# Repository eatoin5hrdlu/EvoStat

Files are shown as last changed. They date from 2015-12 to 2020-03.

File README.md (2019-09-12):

EvoStat:  A PhageStat to support PACE and PATHE Experiments
====
Software and Hardware for an automated platform for PACE and PATHE experiments.

PATHE (Phage-Assisted Three-Hybrid Evolution) is our enhancement to PACE (Phage Assisted Continuous Evolution) which was described by Kevin M. Esvelt, Jacob C. Carlson, and David R. Liu in http://www.ncbi.nlm.nih.gov/pubmed/21478873

This project contains Arduino code for a Host CellStat (Turbidostat), Sample Collector, and Lagoons
as well as the server software to provide an on-screen interface to Temperature, Turbidity, Flowrate,
and Sample Collector control and Web interface.  The goal is a remote access, fully automated system with a build cost less than $1000.00. 

SWI-Prolog based web server, GUI, and Turbidostat control software written mostly in Prolog/Xpce with some Python (e.g. pySerial, for a 
portable serial interface to Arduino) and HTML. Bluetooth interface added as foreign function library to SWI-Prolog currently eliminates the need for pySerial. See github.com/eatoin5hrdlu/plblue 

Running EvoStat on a Linux or Windows machine provides an interface for multiple phageStats with Bluetooth connected Arduinos running module.ino (then software defined as Host or Lagoon controller) and a sample collector: Bluetooth connected Arduino running collector.ino. (Using a WiFi camera and bluetooth modules has reduced apparatus wiring by 90%)

A web interface provides a similar interface via the URL:  

    http://<host>:21847/web/pathe.pl

Prerequisite Software
====
- Python2.7
- OpenCV (on Linux add "apt-get install python-opencv")
- SWI-Prolog with Xpce
- Arduino IDE (Processing)
- apt-get install these additional packages
  - python-psutil, ffmpeg, octave, dnsutil  (some other stuff, watch this space).
  - On Linux add : imagemagick (for conversion of image files)
  - apache2-utils: for Web Authentication (encrypted password) Files
  - 

Getting Started
====
1) Clone the EvoStat repo:

    git clone https://github.com/eatoin5hrdlu/EvoStat.git

2) Create a "secrets" file in the EvoStat directory to enable sending of SMS messages

Filename :       secrets
File contents:   { 'login': 'your-email', 'password': 'your-password' }

   Example: For gmail, your-email does not include "@gmail.com"
   Your login is just the first part of your email address
    
3) Clone the plblue Git repository (Prolog interface to Bluetooth communication)

    git clone https://github.com/eatoin5hrdlu/plblue.git
    
    cd plblue
    
    make      ( required packages: libbluetooth-dev and bluez )
    
    make install  (moves the shared library into the ../EvoStat directory

--- MESSAGING (SMS) via Python smstext.py program
Needs package dnsutil for program "dig" to get outside IP address, in order to include a functional URL for the EvoStat to outside users.

File 'secrets' must have login/password for SMS server (e.g. via gmail)

--- LEVEL detection Python/OpenCV

A python program (alevel.py) uses OpenCV to read the liquid levels of the vessels.
Windows and linux versions of #! in ipcam.py appear at the top of the file
It may be necessary to move the correct one to the top. Or call python:

$ python level.py 
$ python level.py show -c 30 sample.jpg
OPTIONS: -c N repeat in N seconds (default 90)
         show   (produce debugging output, including processed images)
         <filename>.jpg    (Read the image file instead of the camera /dev/video{0,1,2} )

------------------
Create stand-alone executable "evostat" (Prolog saved-state)
$ swipl (linux) or swipl-win
:- [c].
:- save_evostat.

Or to maintain terminal access for debugging, start with:

$ swipl(-win)
:- [c].
:- c.

When the interface comes up, you can:
turn off the automatic level sensing with Action -> Stop
turn off the PID volume/flow controllers  Action -> PIDstop
Get back to the Prolog prompt with File -> OK

View the Web Interface with the URL  http://localhost:21847/web/pathe.pl

The unusual port numbers are from the ca. 1995 NetSpeak (WebPhone). My legacy, no longer in use.
Change it in c.pl to 80 or 8080 to appear as a normal web server

--------------
To changing the Icon on a Prolog saved-state on Windows:

    chicon.exe saved.exe myapp.ico myapp.exe

###########################
Procedure for operating the EvoStat:

Sterilize Supply and Drain Valves with 1M NaOH

Install Valves

Autoclave Cellstat and Lagoon vessels

Autoclave Nutrient/Inducers in conainers

Install supply vessels on top of EvoStat and connect to supply valves

Connect supply valves to Cellstat

Open bypass valve to fill Cellstat with Nutrient

Close bypass valve when Cellstat Level is at desired set point (85%)

Inject host cells into Cellstat when target temperature is reached.

Normal flow control begins when OD target has been reached.

Infect lagoons with phage.

Regular texts will be sent to report EvoStat status.
	Each text includes the URL to EvoStat status/control page.
Exceptional texts will be sent if:
	1) temperature / turbidity / level / flow out of range
	2) leak has been detected

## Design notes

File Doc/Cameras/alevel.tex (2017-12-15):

\documentclass[10pt,letterpaper]{article}
\usepackage[top=0.85in,left=2.75in,footskip=0.75in]{geometry}
\usepackage{amsmath,amssymb}
\usepackage{changepage}
\usepackage[utf8]{inputenc}
\usepackage{textcomp,marvosym}
\usepackage{cite}
\usepackage{nameref}
\usepackage[pdftex,
            pdfauthor={Peter Reintjes},
            pdftitle={EvoStat Level Monitoring System},
            pdfsubject={Level Monitoring},
            pdfkeywords={OpenCV Python},
            pdfproducer={Latex with hyperref},
            pdfcreator={pdflatex}]{hyperref}

\hypersetup{
    colorlinks=true,
    linkcolor=blue,
    filecolor=magenta,      
    urlcolor=cyan,
}
\usepackage[right]{lineno}
\usepackage{microtype}
\DisableLigatures[f]{encoding = *, family = * }
\usepackage[table]{xcolor}
\usepackage{array}
\usepackage{listings}
\newcolumntype{+}{!{\vrule width 2pt}}
\newlength\savedwidth
\newcommand\thickcline[1]{%
  \noalign{\global\savedwidth\arrayrulewidth\global\arrayrulewidth 2pt}%
  \cline{#1}%
  \noalign{\vskip\arrayrulewidth}%
  \noalign{\global\arrayrulewidth\savedwidth}%
}

% \thickhline command for thick horizontal lines that span the table
\newcommand\thickhline{\noalign{\global\savedwidth\arrayrulewidth\global\arrayrulewidth 2pt}%
\hline
\noalign{\global\arrayrulewidth\savedwidth}}

\usepackage{enumitem}
\setlist{nosep}
\raggedright
\setlength{\parindent}{0.5cm}
\textwidth 5.25in 
\textheight 8.75in

\usepackage[aboveskip=1pt,labelfont=bf,labelsep=period,justification=raggedright,singlelinecheck=off]{caption}
\renewcommand{\figurename}{Fig}

% Remove brackets from numbering in List of References
\makeatletter
\renewcommand{\@biblabel}[1]{\quad#1.}
\makeatother

% Leave date blank
\date{}
% Header and Footer with logo
\usepackage{lastpage,fancyhdr,graphicx,wrapfig}
\usepackage{epstopdf}
\pagestyle{myheadings}
\pagestyle{fancy}
\fancyhf{}
\setlength{\headheight}{27.023pt}
%\lhead{\includegraphics[width=2.0in]{PLOS-submission.eps}}
%\rfoot{\thepage/\pageref{lastpage}}
\renewcommand{\footrule}{\hrule height 2pt \vspace{2mm}}
\fancyheadoffset[L]{2.25in}
\fancyfootoffset[L]{2.25in}
% customize
\lfoot{\sf Innatrix Internal Document}

\begin{document}

\title{EvoStat Level Monitoring System}
\author{Peter Reintjes}
\date{\today}
\maketitle

\vspace*{0.2in}
\begin{flushleft}
.jpg}
\end{flushleft}

{\it The EvoStat liquid-level control system consists of two distict parts: Monitoring and Control, which are accomplished by separate programs.  This report focuses on the monitoring program (alevel.py), a Python/OpenCV\cite{opencv} program which observes and reports the levels of vessels within the main EvoStat chamber.  The main EvoStat control program requires this level information to maintain volumes, cell density, and flow rates in the various chambers to support experiments in the continuous evolution of bacteriophage\cite{pace}.}

\section*{Introduction}

The {\bf alevel.py} program is a Python program which takes an image from a digital camera and determines the individual liquid levels in transparent containers within the image.  The EvoStat system uses the program to report the liquid levels of up to five vessels, one 2-liter host-cell cultivator and four 250mL lagoons.

\section*{Level Detection in the EvoStat}
Whenever a level reading is to be taken, {\bf alevel.py} reads a text file {\bf .previous} which specifies for each vessel:

\begin{enumerate}[itemsep=1pt, topsep=2pt, partopsep=0pt]
\item Area of the image in which the meniscus appears
\item Recommended intensity amplification (images to sum)
\item Recommended contrast (gain and threshold) settings
\end{enumerate}
Here is an example of the {\bf .previous} file containing the recommended settings and vessel locations.  The {\bf reticule} entry refers to the red reference LEDs used for level calibration.  The absence of a bounding box indicates that the reticules can be anywhere within the image area.
\begin{verbatim}
# (Vessel,oldPt,BBox,Contrast-iter, Contrast-mul, Contrast-off,')
#               Erode-iter, Dilate-iter, Amplify-iter, Amp-factor')
# (name, (x,y), ((uy,lx),(ly,rx)), 1, 1.2, -80, 2, 2, 3, 0.7)')
# lagoon   1, 1.5972, -90, 2, 2, 3, 0.7)]
[('reticule', 0, 1.4, -80, 180, 1, 4, 3, 0.4),
 ('host0', (47, 22), ((40, 120), (214, 380)), 1, 1.2, -80, 2, 2, 2, 0.4),
 ('lagoon1', (84, 71), ((340, 50), (460, 260)), 1, 1.1, -110, 2, 2, 3, 0.7)]
\end{verbatim}

The file is named {\bf .previous} because the program will try these recommended values for contrast and intensity settings but vary them until it can get a good level reading.  If the user specified the {\bf update} option when invoking {\bf alevel.py} a new file will be written with the contrast and intensity values actually used.  The next time the program is run, these settings may be able to get a good level reading without the need to vary them.  The program may also adjust the bounding boxes to be smaller and centered on the meniscus that was actually measured.

\subsection*{Camera Settings}
The unusual (low) light conditions inside the EvoStat may require a camera to be initialized with specific exposure, contrast, and saturation settings. While many cameras have automatic exposure modes, detection can often be improved with custom settings to match the dark conditions and our use of primary colors: red for the reticules, green for the liquid menisci.

One of the legacies of
Windows\textsuperscript{\textregistered}
and other closed systems is that each camera manufacturer has to produce a program for the (closed) operating system for each of their cameras.  Linux systems have kept up pretty well with a tool called guvcview which knows about many cameras -- especially the cheap ones.  This interactive program can be used to modify settings on many cameras and save those settings in a file with the {\bf .gpfl} suffix.  This file can be used to initialize the camera when the program starts by calling the program {\bf uvcdynctrl}.

After making the necessary image adjustments to the camera at {\bf /dev/video0} with {\bf guvcview} and saving the settings in the file {\bf evostat.gpfl}, the level monitor program (or any other process) can run the following command to restore the camera to these settings:
\begin{verbatim}
       /usr/bin/uvcdynctrl -L evostat.gpfl --device=/dev/video0
\end{verbatim}

Although the EvoStat programs are otherwise portable between Linux and
Windows\textsuperscript{\textregistered}
systems, we know of no comparable program that would make this method
of camera initialization available on
Windows\textsuperscript{\textregistered}
systems.

\subsection*{Alignment}
It is not necessary to align the camera precisely as long as it has a clear view of the reticule column and that the regions specified for each vessel in the {\bf .previous} file surround a sufficient horizontal region of the meniscus.

\subsubsection*{The Reticules}
The {\bf reticules} are movable red LED assemblies on a black column inside the EvoStat. The upper assembly should be aligned with the target liquid level in the upper, or host-cell cultivation chamber, while the lower assembly should be aligned with the target level for the lagoons.  The EvoStat is designed so that all of the lagoons are on the same level, hence we only need one reticule to provide a reference for the lagoon levels.

\begin{wrapfigure}{L}{0.25\textwidth}
\centering
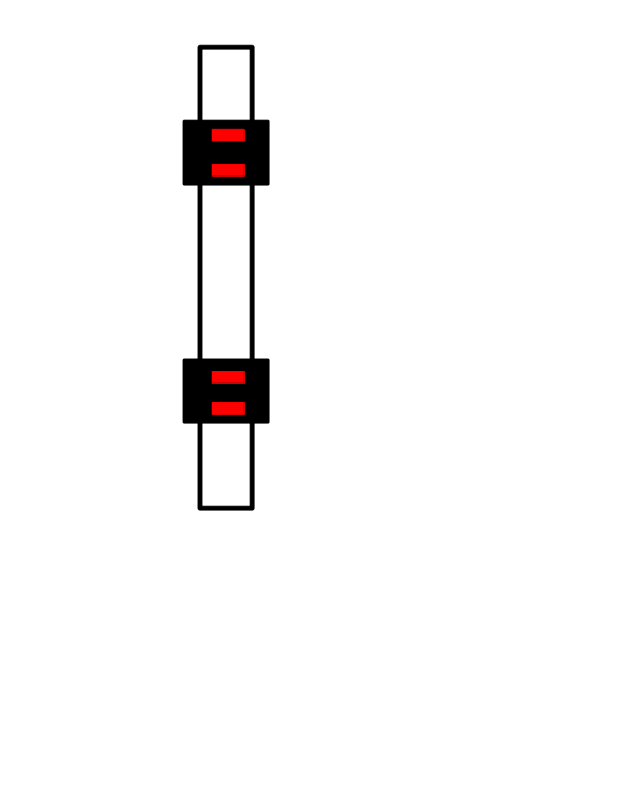
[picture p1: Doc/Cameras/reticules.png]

\caption{\label{fig:reticules}Reticules}
\end{wrapfigure}

Reticule placement does not directly specify the level being controlled.  Level control is relative to the reticules and may be set to maintain a level at an offset above or below the level of the reticule. In the simplist case, however, it is convenient to position the reticule assembly so that the two red bars surround (above and below) the desired liquid level.  This corresponds to a zero offset for the liquid level to be maintained.

\subsubsection*{Vessels}

For each vessel, the
{\bf .previous}
file has a bounding box defining the region of the image where the meniscus will be visible, and intensity and contrast settings. Once
{\bf alevel.py}
reads this file, it will try to detect the horizontal liquid level in each of these regions using the contrast and intensity settings found in the file. However, if this fails it will vary each of these parameters by positive and negative factors in 10\% increments until it gets a good reading (or a specified number of attempts have been made).  With the {\bf update} option,
{\bf alevel.py}
will re-write the new values to the
{\bf .previous}
file.

\subsection*{Lighting}

The various EvoStat vessel holders shine light from bright green LEDs up into the liquid containers. When liquids are clear (e.g. uninoculated), this results in a reflection off the meniscus which can be used to determine the liquid level. However, the system works most reliably with the turbidity of a growing culture which is the primary mode of EvoStat operation.  Until the image processing has been improved, we should consider that accurate level readings will only occur when there is active culture in the vessels (e.g. not during setup and sterility testing).

Level readings also fail when the EvoStat chamber is opened, and therefore exposed to normal room lighting.  While the ability to darken the room can substitute for a closed chamber, we haven't had that luxury since being evicted from the Tod Vision's gardening tool shed in the Genome Sciences Building.

If a good level reading is not possible, calls to the level monitoring program return no results and the EvoStat reacts as if the last good reading was repeated.  As with all other parts of the EvoStat, the system is designed to operate with the current settings through any loss of telemetry.

\subsection*{Growth Conditions}
Under actual growth conditions, the liquids are turbid and create a lot of scattered light.  The LEDs below the vessel must be bright enough to completely illuminate the contents.  This is particularly important for the large, upper chamber because the light source is at the bottom of the 2-liter container. In particular, we do not see a high-contrast meniscus when the volume is near the overflow drain (1.5 liter level).

\section*{Next Steps}

Now that the level reporting program is relatively stable, a complete code-review re-write is in order.  Duplicated code can be eliminated in the horizontal line detection and image amplification subroutines. Red/reticule and Green/Level readings had minor differences which were best debugged using separate implementations.

Produce level information in resolution independent coordinates so that they are the same whether a 640x480 or 1280x1024 image is available. Or, alternately, provide image resolution information with the data and allow the recieving program to do the coordinate mapping.

\begin{enumerate}[itemsep=1pt, topsep=2pt, partopsep=0pt]
\item Review/re-write code: 800 lines of Python, can probably be halved.
\item Make level data resolution independent
\item Automate camera settings under Windows\textsuperscript{\textregistered}
\end{enumerate}

\bibliographystyle{unsrt}
\bibliography{alevel}{}

\pagebreak

\section{Appendix: alevel.py source code}
\newcommand*{\SrcPath}{../..}
\lstinputlisting[language=Python]{\SrcPath/alevel.py}
\end{document}

\input{\MyPath/chap1/ch1.tex}

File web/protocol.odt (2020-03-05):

EvoStat (PACE) Protocol

Huxley Run #2 January 7-11 2019

January 2019

Su Mo Tu We Th Fr Sa

1 2 3 4 5

6 [7 8 9 10 11 12 ...]

13 14 15 16 17 18 19

20 21 22 23 24 25 26

27 28 29 30 31

[Notes]

7 L of LB (2X autoclave. Final cycle 45-min)

Kanamycin (water) : 30ug/mL →30mg/L → 210mg/7 L

JW5856 requires Kanamycin for the TRXA- “deletion” which is an insertion of kanamycin resistance gene.

( 30ug/mL is from Baba et al. 2006 )

Tetracycline : 10ug/mL → 10mg/L → 70mg/7 L

( for F+ maintenance )

Chloramphenicol (either, but ethanol better): 25ug/mL → 25mg/L → 175mg/7 L

Carbenicillin (water) : 60ug/mL → 60mg/L → 420mg/7 L

Glucose 175mL 20% by weight = .45% in 7 L (27mM)

HG-Selection Run in EvoStat: repeat of the previous run but with better flow control.

Cells: JW5856:t3trxA:MP6

Phage: M13T7rnaP

Ref: Jiarui’s lab report of Nov 13.

1. Grow JW5856+MP6 to 0.5 OD in chamber 1.
2. Transfer 40 ml from chamber 1 to lagoon
3. Add sufficient arabinose to bring the lagoon to 0.3% arabinose
4. ?? alternative here is to use ATc at 30 ng/ml
5. Add M13RNAP to the lagoon at an MOI of about 1.0 (previously used 0.5)
6. Start the run with flow through the lagoon at 30 ml per hour

Autoclave nutrient (LB) twice over the weekend, added Kanamycin, Tetracyline, Carbenicillin, Chlorophenicol, and 25mM Glucose (175mL of 20% by weight for 7L).

Inoculate with cells Sunday Evening

Infect with Phage Monday.

[ Previous run had one day sterility test, room temperature, without antibiotics ]

JW5856-2 M13 T7 RNA pol evolution run (Jan 6 to Jan 13 or extend…)

1. Pre-mutagenize M13T7RNAP:

Martha has grown M13 RNAP on S1030: MP6 in 2XYT added with tetracycline, chloramphenicol and 25mM arabinose for 5 hours, and clarified in 30 min/3.5k. The titer is 1.5E+10 pfu/ml.

2. Grow JW5856 T3-trxA+MP6 to 0.5 OD in chamber 1.
3. Transfer 40 ml from chamber 1 to lagoon.
4. Add sufficient arabinose to bring the lagoon to 0.3% arabinose.
5. Add M13RNAP to the lagoon at an MOI of about 1.0.
6. Make the virus and JW5856 cells incubate for 1. 5 hours in the lagoon.
7. Start the run with flow through the lagoon at 30 ml per hour.
8. Make the run continuously for at least 7 days. Every day, take samples to check Hibit expression, plaque on S1030, JW5856-2, and JW5856-2 MP6+T3 trxA.
9. When we see big increase for Hibit expression, or many plaques on S1030 and/or JW5856 MP6+T3 trxA, extract DNA from M13 RNAP, and do sequencing.

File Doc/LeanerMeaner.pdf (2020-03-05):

## Instructions for manual PACE/PATHE setup using peristaltic pumps and large incubation chamber

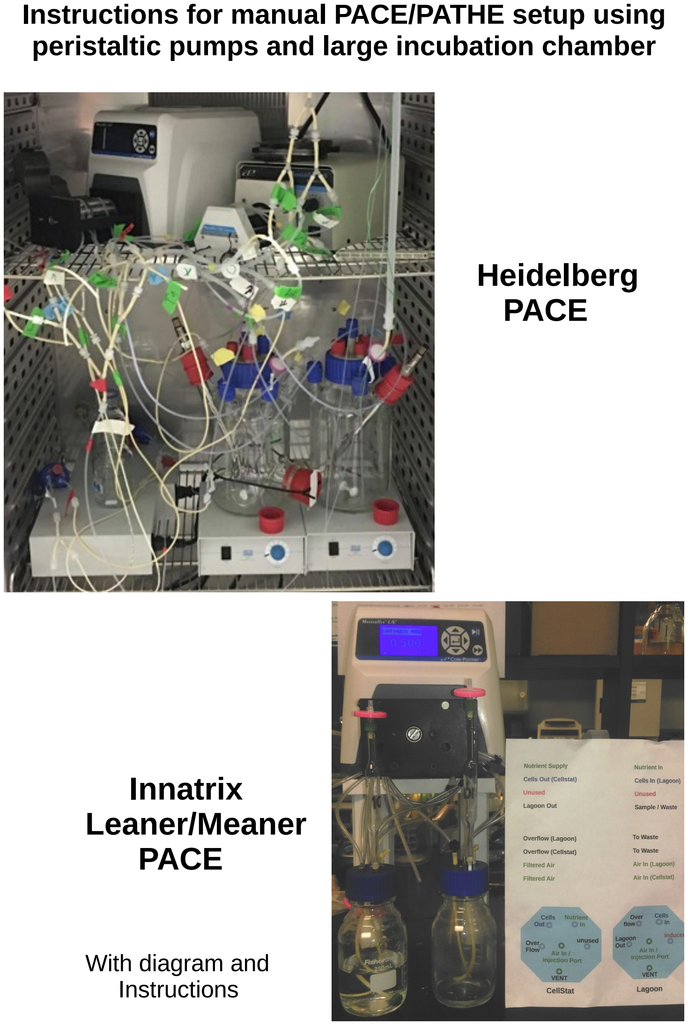
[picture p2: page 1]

## Heidelberg PACE

## Innatrix Leaner/Meaner PACE

### With diagram and Instructions

This setup uses seven (7) of the eight peristaltic pump channels. There may be hours between steps as they involve autoclaving, flling, and sterility testing. Filling steps can be accelerated by changing the pump speed.

Starting at the pump face and moving outward toward the observer, the pump channels are numbered 1-8. With the default mode of the pump moving liquid from left to right, we designate the ends of the tubes as [a] left/input and [b] right/output.

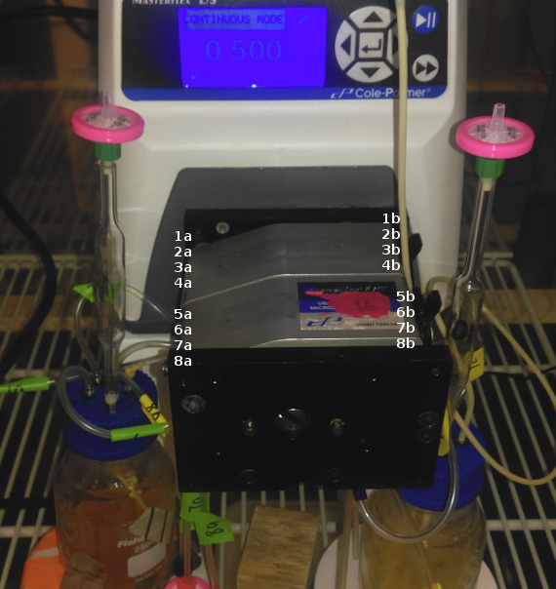
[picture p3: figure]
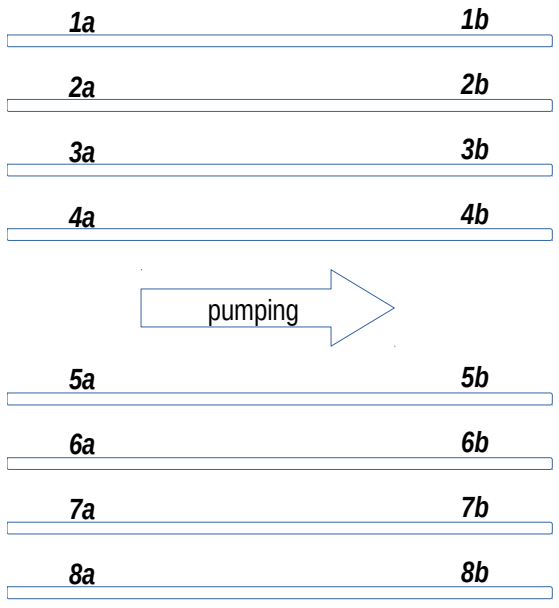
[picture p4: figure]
pumping

In the continuous evolution experiment, we make the following assignments.

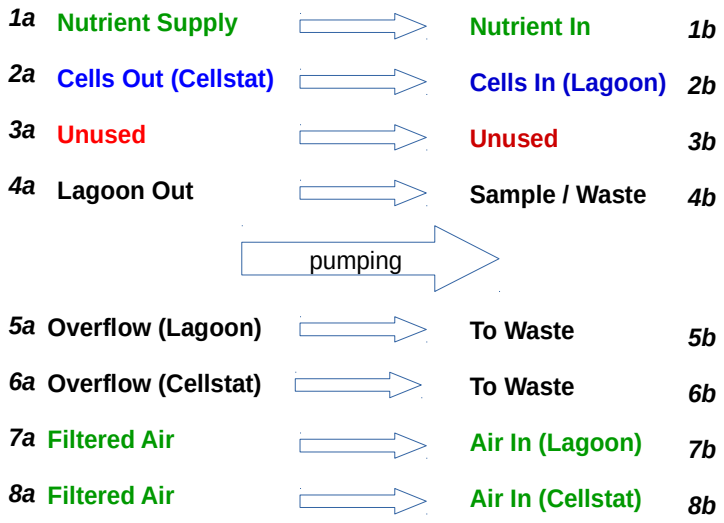
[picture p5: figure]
Nutrient Supply; Cells Out (Cellstat); Unused; Lagoon Out; Nutrient In; Cells In (Lagoon); Sample / Waste; Overflow (Lagoon); Overflow (Cellstat); Filtered Air; To Waste; Air In (Lagoon); Air In (Cellstat); pumping

Step 1: Sterilizing the Equipment

Autoclave vessels and place the [a] left/input ends of all pump tubes into an ethanol supply. Place [b] right/output ends of tubes into an ethanol receiver. Start pump.

Step 2: Initial Connections and Air Vents

With vessels still in the Autoclave, attach new 0.45 micron flters to the vent burets. Also install and verify direction of vents in Nutrient and Inducer vessels. Preferred air-fow direction in the 0.45 micron flters is into the luer connector and out through the nipple. Air intake is vital for Nutrient and Inducer supplies, while Air exhaust is required for CellStat and Lagoon. Each vessel must have either an intake or an exhaust flter.

Move vessels to incubator and place CellStat and Lagoon on stirring plates under pump.

Leave tubes 2a, 2b, and 4a in ethanol while removing other tubes from ethanol and connecting according to the labels in the diagram. Don’t forget to insert new 0.45 micron flters into tubes 7aa and 8a (SSterile Air Intake).

Allow CellStat to fill with Nutrient. Then, with heating, aeration, and mixing operational, remain in this state to verify CellStat sterility by turning the pump of (Note: this also turns aeration off, but if nothing is growing, the rate it isn’t growing doesnt matter).

Step 3: Innoculate CellStat

Add host cells to CellStat and wait for growth to OD600 of 0.4. Remove the buret air vent temporarily to inject cells. Pump is still of.

Step 4: Fill Lagoon

With CellStat at target volume, connect tubes 2a (SCells Out / CellStat) and 2b (SCells In / Lagoon) to begin flling Lagoon. Pump must be turned on.

Step 5: Infect and Start Continuous Flow

With Lagoon at target volume, infect Lagoon with phage via buret/air flter vent port and connect 4a (Lagoon Out) while making sure that 4b is connected to the waste/sample collector. Connect Inducer from the secondary pump (Snot shown) which will be supplying additional chemicals to the Lagoon.

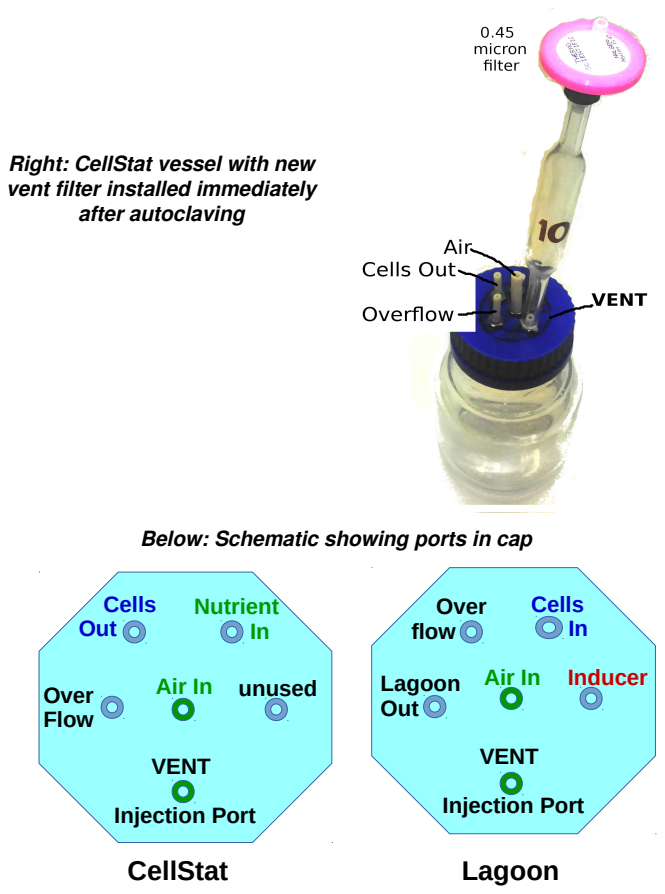
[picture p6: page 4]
after autoclaving; Lagoon Out; Over flow; Cells In; Inducer; VENT; Injection Port; Air In; Cells Out; Nutrient In; Over Flow; unused; CellStat; Lagoon

Right: CellStat vessel with new
vent filter installed immediately

Below: Schematic showing ports in cap

### Nutrient Supply

### Cells Out (Cellstat)

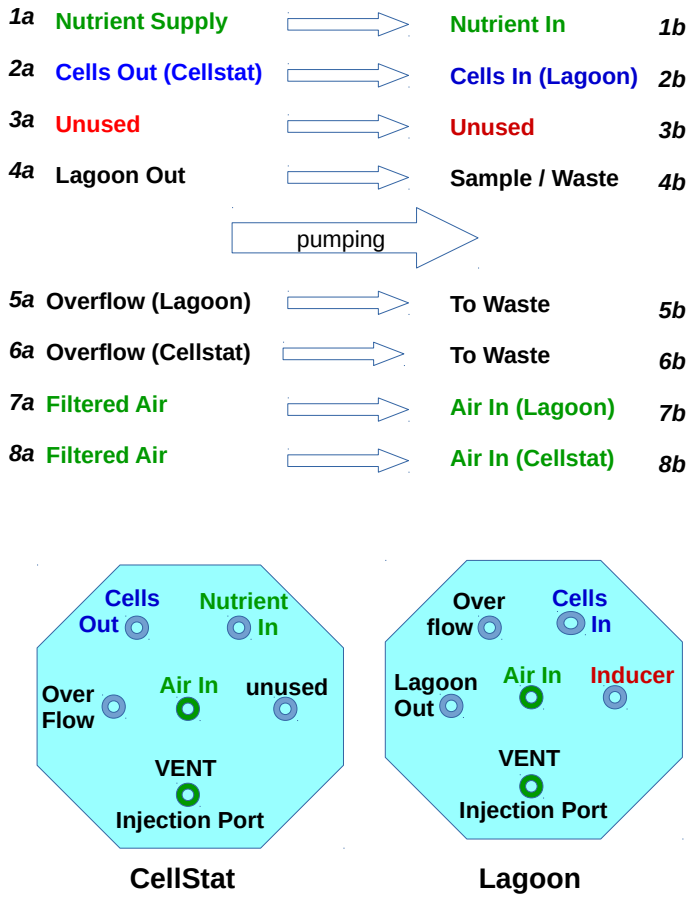
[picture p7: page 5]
Unused; Lagoon Out; Nutrient In; Sample / Waste; Overflow (Lagoon); Overflow (Cellstat); Filtered Air; To Waste; pumping; Over flow; Cells In; Inducer; VENT; Injection Port; Air In; Cells Out; Over Flow; unused; CellStat; Lagoon

Cells In (Lagoon)

Air In (Lagoon)

Air In (Cellstat)

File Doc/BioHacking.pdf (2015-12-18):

## Bio-Hacking:

### Evolution as a Tool

A short talk on a new technology for protein engineering
and

Building a PhageStat
A longer talk on building the necessary devices

Peter Reintjes

Evolution as a Tool

PACE - Phage Assisted Continuous Evolution (Esvelt et al. Nature, April 2011) Use a virus to evolve a custom protein

This requires you to build a PhageStat to maintain a population of evolving virus (Husimi 1989)

Off the shelf hardware for about $30,000
- or -
DIY hardware + open source software ~$1000

## Motivation

- Shigella kills 1,000,000 people – mostly children in the developing world – every year
- Shigella without the extracellular proteases Pic and SepA is harmless
- Hypothesis: We can evolve protease inhibitors with strong binding affinity to Pic and SepA to diminish Shigella's virulence
- Hypothesis: Engineered proteases produced by lactobacillus or other probiotic could provide inexpensive, long-term immunity

### Protein-based pharmaceuticals

- Large proteins have reduced side-effect potential over small-molecule drugs which cross metabolic barriers and have more interaction potential
- Proteins can be more easily metabolized without stressing renal function
- Proteins degrade more quickly in the waste stream
- Binding affinity is the principal characteristic of metabolic processes and pharmaceuticals
- Increased binding affinity would lower dosage for any protein therapeutic

## Evolution = Mutation + Selection

- Virus replicates inside E. coli which uses an error-prone DNA polymerase to increase mutations
- E. coli rewards improvements to evolving protein by providing the fusion protein that increases viral infection

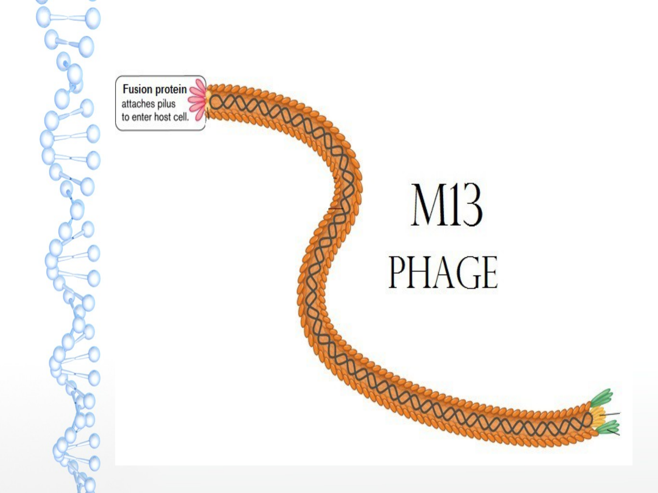
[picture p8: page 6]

PACE: Phage Assisted Continuous Evolution

- M13 virus (phage) with the sequence to evolve replacing its fusion gene
- E. coli with two extra plasmids (chromosomes)

− Mutation: Arabinose activated mutagenesis (error-prone DNA polymerase) − Selection: M13 fusion gene activated by
a particular protein interaction
- E. coli host cells flow through “lagoons” with populations of evolving viruses

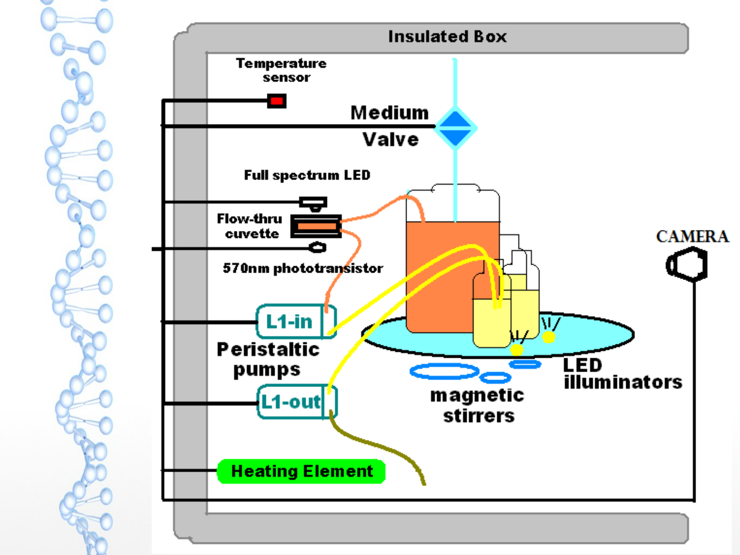
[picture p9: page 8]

Experiments can run from four to six days requiring reliability and automation

(10³

generations X 10⁹

mutations)

Off-the-shelf solution requires integration as well as more hands-on oversight

(three shifts of lab personnel?)

## Building a PhageStat

A device to maintain a stable population of bacterial phage (virus)

To build a Phagestat, you need:

1. A Cellstat to produce (E. coli) host cells
2. Control of output and multiple input flows

Inputs: Host cells and inducers

Output: Sampling and waste output

## Building a CellStat

A device to maintain a
continuous supply of host cells (E. coli)
1. A Thermostat to maintain the culture at 37˚C
2. A Turbidostat to maintain cell density with nutrient dilution
3. Isolation from bacterial phage:
Cellstat output is the Phagestat input

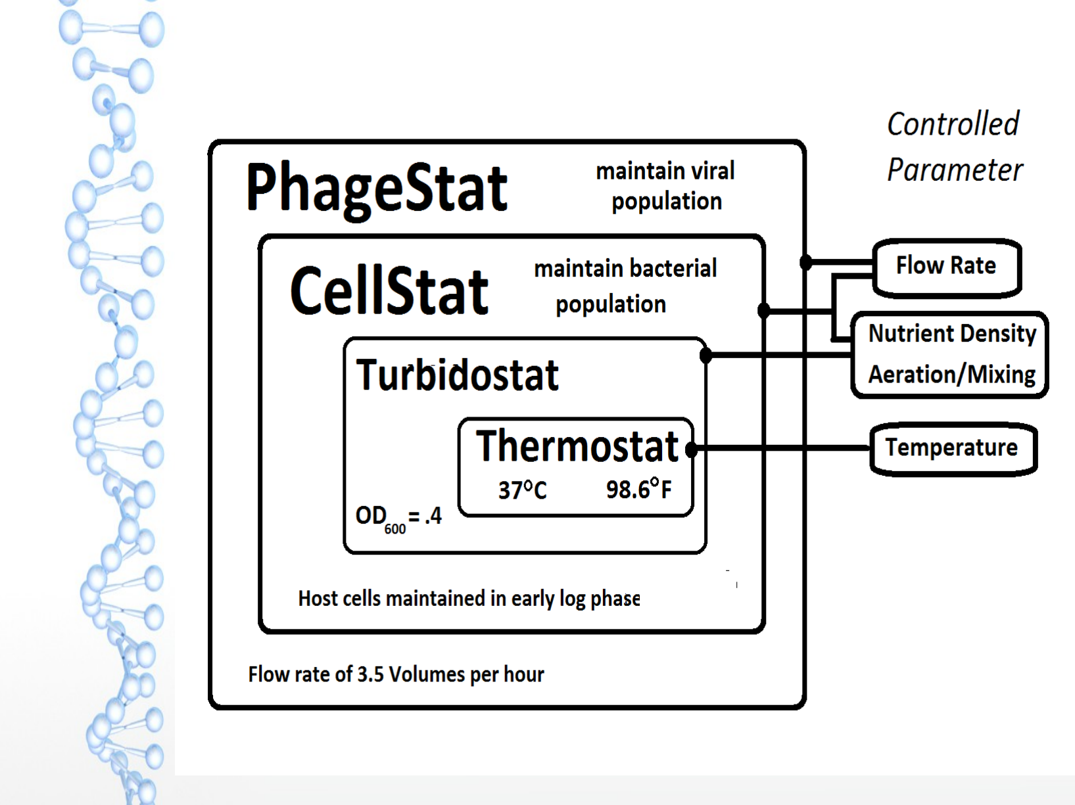
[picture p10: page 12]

## Flow rate control

The ideal Phagestat has:

1. A flow rate high enough to force host cells through in one cell lifetime, so the only mutations are in the phage sequence
2. A flow rate slow enough to prevent washout of phage even with large variations in the viral reproduction rate

## Design Principle

Replace expensive, precision equipment which is not fixable / hackable by team members with extremely simple hardware and sensors and then produce the required precision with computer control

Arduino micro-controller
Raspberry Pi / Linux
Webcam
Python programming language OpenCV image processing software PIR (Passive InfraRed) temp sensor LEDs, resistors, motors, magnets Discarded flatbed scanner
Styrofoam shipping containers PVC plumbing hardware
3D printer

Raw materials

## Turbidostat version 1.0

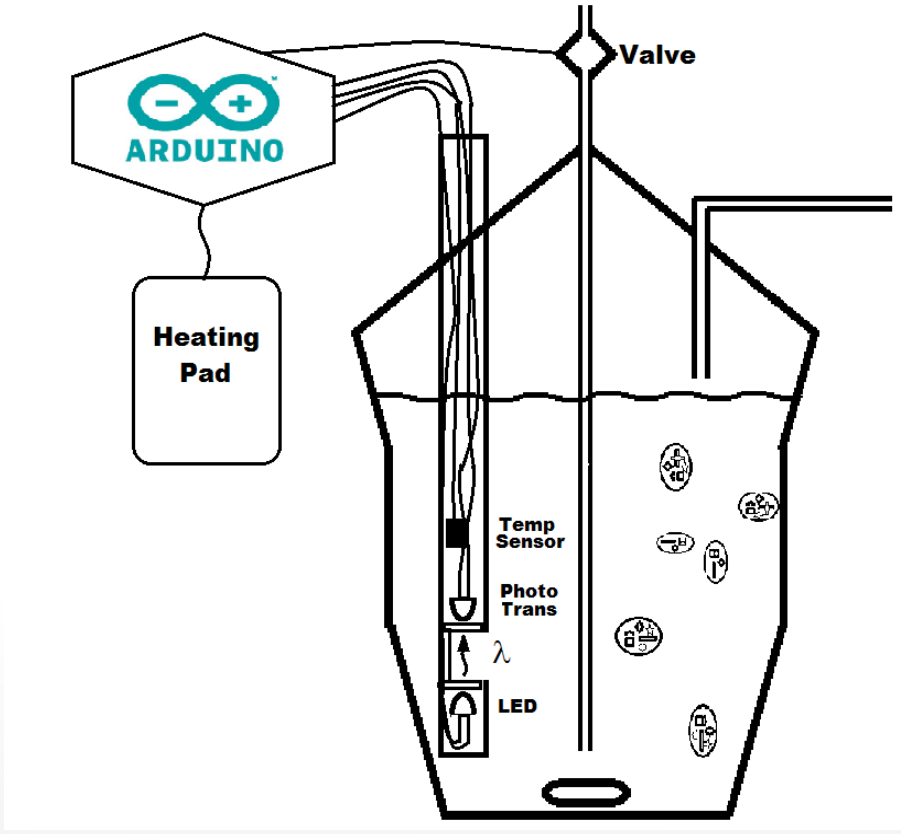
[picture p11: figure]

## Non-contact level-sensing

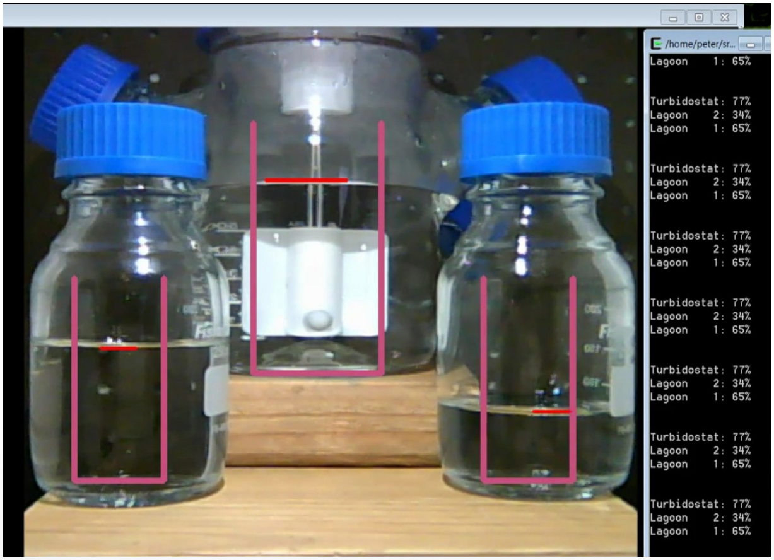
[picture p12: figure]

Material Costs for a “PACE capsule” $1035*

- Raspberry PI main computer ($40)
- Wide-angle USB or IP Camera ($100)
- Arduino Mega 2650 ($35)
- PIR (non contact) Temperature Sensor ($50)
- Laser, LEDs, Photo transistor ($20)
- Insulated boxes (Uline Styrofoam) ($70 X 2)
- Heating Elements ($30 + $60)
- Stirring Motors w/magnets ($10 X 5)
- Aquarium air pump ($35)
- Rotary valve motor, valves, peristaltic pumps ($150)
- Miscellaneous Hardware-PVC ($100)
- 5V and 12V Power Supplies ($20)
- Glassware ($200)
- Tubing + Nutrient (operating cost)
* Retail, single quantity prices

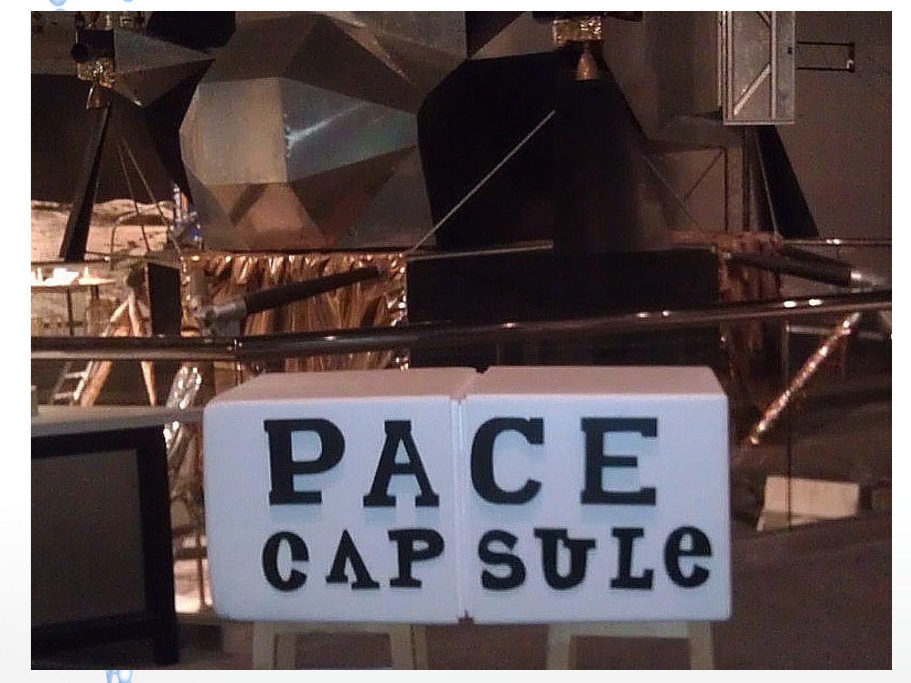
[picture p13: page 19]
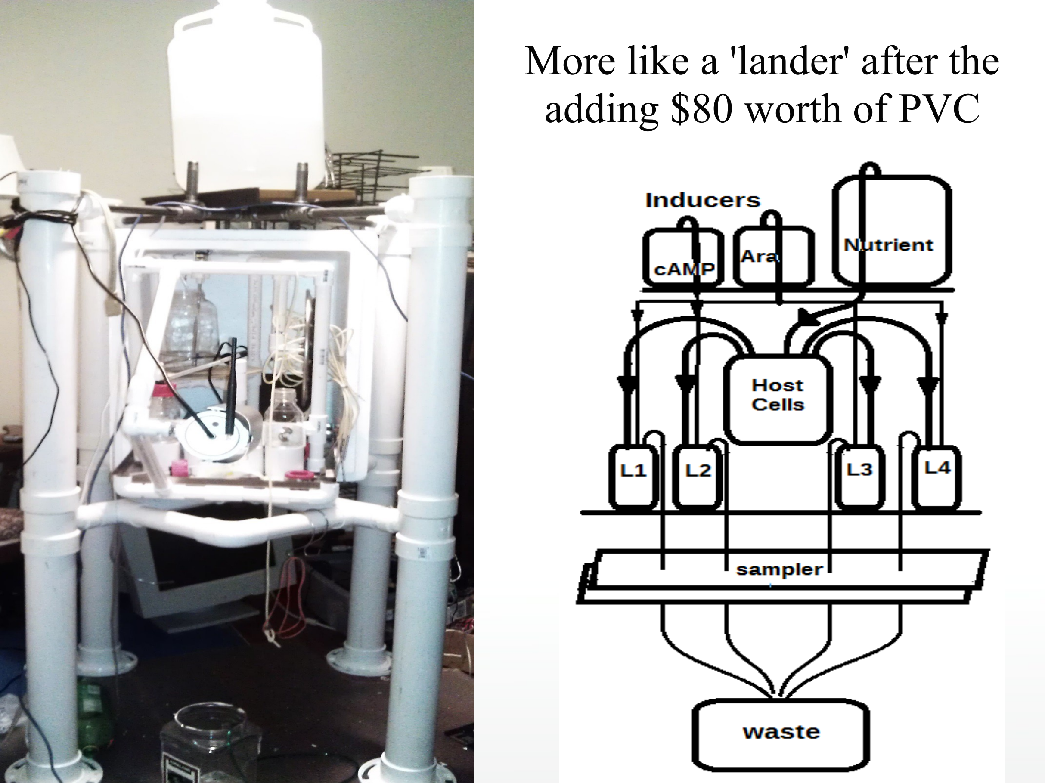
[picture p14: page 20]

More like a 'lander' after the adding $80 worth of PVC

- A multi-channel Autosampler from a flatbed scanner plus 3D printed parts
- Computer controlled heater and magnetic mixer for biological samples
- Using a 3D printer to create a 16-channel computer-controlled valve for ~$50
- Low-voltage heating for liquid environments

## Hardware Projects

- Measuring fluid levels with OpenCV
- Detecting bioluminescence with OpenCV and a USB camera
- Writing an Arduino PID controller (PID = Proportional / Integral / Differential)

## Software Projects

Summary:

Styrofoam boxes for thermal isolation Black garbage bags for optical isolation Stovetop coils, printer power supplies,

### 50 ohm 10W power resistors for

low-voltage heating (up to 40ºC) motor($1),T-nut,2 magnets = Magnetic stirrer Camera + image processing = sensors Pizza crisper pan, motor, 3D parts = valves Flatbed scanner, motor, 3D parts = sampler $10 Ardweeny controlling a heat gun

Problems:

Bioluminescence detection requires expensive high-voltage photomultiplier tubes and complex plumbing

3D printers can't make stainless steel parts

DIY electronic sensors must be sterile, but fail after being autoclaved repeatedly

The $10,000 environmental chamber failed catastrophically mid-experiment

Silicon/Tyvek tubes ruptured after several days in a constantly running peristaltic pump

Problem:
Bioluminescence detection requires expensive high-voltage photomultiplier tubes and complex plumbing

Solution:
In a dark room, point a heat gun at a $20 webcam and take a picture, this is your camera's noise image

Take 100 pictures in total darkness and add the frames up using: +Green–(Red+Blue)/2 finally, subtract the noise image

Problem:

3D printers can't make stainless steel parts

Solution:
Perhaps you simply need parts with stainless steel edges or surfaces

Buy uncoated stainless steel welding rods $6/lb and design plastic 3D parts with openings for rods and/or plates

Problem:

DIY electronic sensors must be sterile, but fail after being autoclaved repeatedly

Solution:
Use non-contact sensing
PIR (passive InfraRed) Temperature sensor Camera, laser and LED lighting, OpenCV image processing for turbidity(cloudiness), bioluminescence, and level sensing

Problem:
The $10,000 environmental chamber failed catastrophically mid-experiment Solution:
LM35DZ temperature sensor ($1.50) Ardweeny ($10) running PID algorithm 1500W heat gun from Lowes ($25) with a solid-state relay ($10)

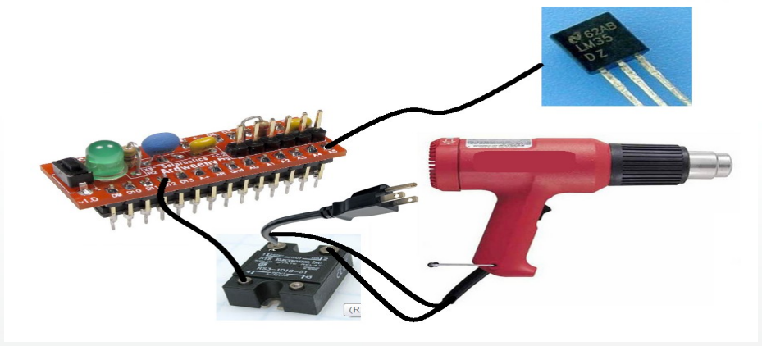
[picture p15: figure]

Problem:

Tyvek tubes ruptured after several days in a constantly running peristaltic pump

Solution:
Design the system for gravity/siphon flow and use peristaltic pumps for priming Peristaltic pumps now only run for a fraction of the total experiment duration

- ApE – an Open Source plasmid editor
- PCR Thermocycler ($25): Ardweeny,Peltier
Junction, Fan,drilled aluminum block

●Gibson and Gateway assembly reagents

- Phage Assisted Continuous Evolution
- SPATEs*: The Achilles Heel of Microbial Pathogens? Tendon

*Serine Protease AutoTransporters of Enterobacteriaceae

## BioHacking

## Know Wonder Moment

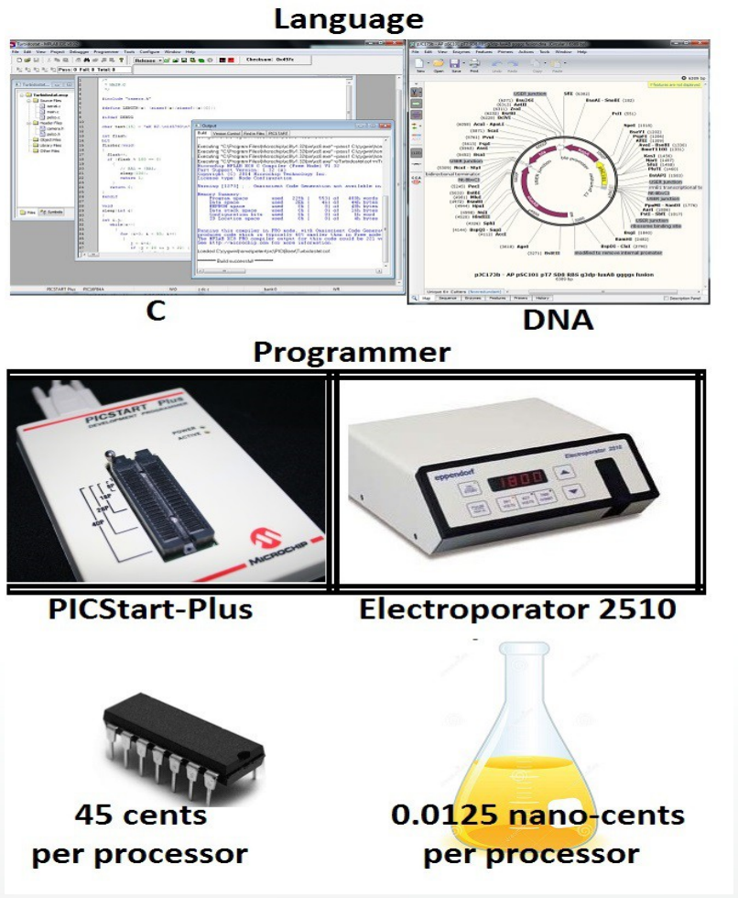
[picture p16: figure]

# Details

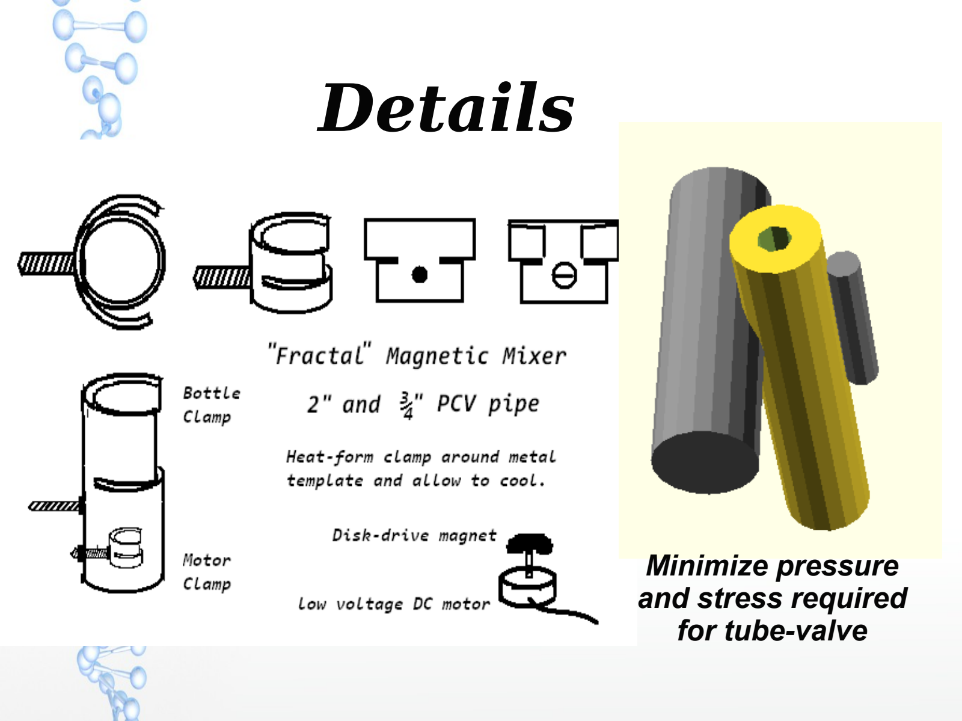
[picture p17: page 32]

Minimize pressure
and stress required
for tube-valve

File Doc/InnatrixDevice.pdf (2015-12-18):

Title: A Laboratory Apparatus for Continuous Macromolecular and Biological Evolution

References:

Selection and Evolution of Bacteriophages in Cellstat, Yuruzu Husimi, Advances in Biophysics, Vol. 25, pp.1-43 (1989).

A system for the continuous directed evolution of biomolecules,Esvelt KM, (http://www.ncbi.nlm.nih.gov/pubmed?term=Esvelt%20KM%5BAuthor%5D&cauthor=true&cauthor_uid=21478873) Carlson JC, (http://www.ncbi.nlm.nih.gov/pubmed?term=Carlson%20JC%5BAuthor%5D&cauthor=true&cauthor_uid=21478873) Liu DR, (http://www.ncbi.nlm.nih.gov/pubmed?term=Liu%20DR%5BAuthor%5D&cauthor=true&cauthor_uid=21478873) Nature. (http://www.ncbi.nlm.nih.gov/pubmed/21478873#) 2011 Apr 28;472(7344):499-503. doi: 10.1038/nature09929. Epub 2011 Apr 10.

pH Indicator, Wikipedia, http://en.wikipedia.org/wiki/PH_indicator

Background of the invention:

Macromolecular engineering can employ the mechanisms of evolution – mutation and selection – to discover novel genetic sequences with desired properties. Earlier means consisted of separate steps for mutation, selection, and cloning, with one or more manual steps, limiting the number of complete cycles to a few per day. Recent advances use continuous cell cultivation techniques, such as a cellstat, to create an environment for continuous evolution. One such method, Phage Assisted Continuous Evolution (PACE), employs the evolution of a bacterial virus with a generation time on the order of a few minutes. In the span of this cycle, all three steps of the evolutionary process – mutation, selection, and reproduction – are carried out without the need to manually isolate or remove any of the reactants. A requirement for this process is the relatively long-term maintenance of the environmental conditions required by the organisms or macromolecules involved.

Just as the simplest device to control a heating or cooling device from the feedback provided by a temperature sensor is called a thermostat, devices for controlling chemical concentrations, cell concentrations, and active bacterial virus populations are given the names chemostat, turbidostat or cellstat, and phagestat. In each case, particular measurements correlated with the condition being maintained must be sensed to provide feedback for the control of temperature, nutrient concentration, flow rate, pH, or other condition.

Sensors for properties such as temperature, pH, and reagent concentration often require contact with the materials involved. In the case of biological systems, this can require the sensors to withstand: autoclaving at elevated temperature and pressure, a corrosive environment with chemistry similar to ocean water, and the build-up of bio-film on sensor surfaces. For these reasons, we would prefer to use non-contact means (e.g. optical) to measure environmental conditions.

A turbidostat controls cell density of a cell culture by monitoring the optical density and controlling the inflow of a clear nutrient solution and outflow of cells in solution. For example, the complexity of a phagestat precludes the simplicity of a thermostat, where a single measured quantity controls one parameter. Measured quantities and parameters can interact, as when aeration, necessary to achieve optimal growth rate of the host cell culture, increases acidity by the addition of dissolved carbon dioxide.

Multiple light sources can be used with a single camera to detect the reflected color, degree of light scattering, and light absorption at various wavelengths. Even precise pH measurements can be obtained optically by adding non-toxic indicators and measuring absorbance at two or more wavelengths. PIR (Passive InfraRed) sensors can provide accurate non-contact means to measure temperature.

Summary of the invention:

A system of non-contact sensing means and computer activated controls to maintain multiple environmental conditions including, but not limited to, temperature, turbidity as a proxy for cell density, liquid levels, reflected or transmitted spectra as proxies for chemical concentrations and pH, bioluminescence as a proxy for phage population and macromolecular concentrations.

Although mutation rates can be elevated and the selection process accelerated to the life-cycle of bacterial phage of only a few minutes, evolution experiments require days, weeks, or longer to achieve the desired results. The present invention is intended to increase reliability of such a system through the reduction of moving or wearing parts and eliminating contact with biological materials.

Precise pH measurement is possible by adding to the nutrient stock one or more non-toxic pH indicators which give a suitable color transition at the desired pH setting. A combination of reflected and absorbed spectral information will be used to gain precision.

A system necessary to maintain a stable population of bacterial phage (the evolving species), requires a cellstat subsystem to maintain the uninfected host cell production, which in turn requires turbidostat and thermostatic controls.

Description of the drawings:

Drawing 1: Hierarchy of parameter-controlled subunits from thermostat, turbidostat, and cellstat, to phagestat.

Drawing 2: Elevation View of the Phagestat

(1) Nutrient supply line
(2) Nutrient supply pump
(3) Nutrient supply valve
(4) Host cell supply line
(5) Host cell supply pump
(6) Host cell supply valve
(7) One-to-four line splitter for host cell supply
(8) Host cell supply line for lagoon 1 (one of four)
(9) Compression rod valve for Host cell supply for lagoon 1

(10) Host cell supply cannula for lagoon 1
(11) Inducer supply line
(12) Inducer supply pump
(13) Inducer supply valve
(14) One-to-four line splitter for inducer
(15) Inducer supply line for lagoon 1 (one of four)
(16) Compression rod valve for inducer supply for lagoon 1
(17) Inducer supply cannula for lagoon 1
(18) Outflow cannula for lagoon 1 (one of four)
(19) Compression rod valve for lagoon 1 outflow
(20) Four-to-one line combiner
(21) Outflow valve
(22) Outflow pump

Drawing 3: Lighting and image capture

(1) Meniscus highlight LED for host cell incubator
(2) Meniscus highlight LED for lagoon 1 (one of four)
(3) LED Laser
(4) Full spectrum (white) LED
(5) Multiple monochromatic LEDs
(6) Camera

Description of the invention:

A transparent container to hold a host cell culture.

A source of liquid nutrient sufficient to maintain the maximum flow rate through the system, a multiplicity of supplementary liquid reagents (inducers) which may be added to the containers.

A pump and valve complex, the primer, which can prime (valve closed, pump on) and then maintain (valve open, pump off) sufficient flow to sustain the maximum flow rate required by the system.

A flow control apparatus consisting of a multiplicity of valves controlling the flow of liquid between the outflow and inflow of the host cell container and each of the lagoons.

A host cell container which is elevated with respect to the phagestat containers (lagoons).

A multiplicity of secondary containers (lagoons) containing a population of bacteria and bacterial phage, each of said lagoons having one or more inputs from and one or more outputs to the flow-control apparatus.

A non-contact (IR) temperature sensor, camera, computer, and image processing software to provide real-time information about the temperature, levels, turbidity, reflected and absorbed spectra, and luminescence of the liquid in a multiplicity of transparent containers.

A heating unit in contact with the primary host cell container. Said heating unit being controlled by the computer control system.

An aeration unit producing pressurized air to be conveyed to the bottom of the host cell container and released into the cell culture.

Immersion or magnetic mixing means for each of the transparent containers.

Means to control lighting in the form of yellow light projected up from beneath the transparent containers to illuminate the meniscus of the liquid in the container, a laser projecting into the transparent host cell container from the side, multiple monochromatic sources directed at the camera from the far side of the transparent containers, and a full spectrum light from the camera's direction to provide visual monitoring of the apparatus.

A liquid sensing device in the bottom of the apparatus to detect leaks and a means to react to said leaks by shutting off the flow of liquid and means for reporting the condition of the apparatus.

Claims:

Claim 1: Simultaneous liquid level detection for multiple transparent containers consisting of an edge detection algorithm from the set {Marr-Hidreth, Roberts cross, (http://homepages.inf.ed.ac.uk/rbf/HIPR2/roberts.htm) Sobel, (http://homepages.inf.ed.ac.uk/rbf/HIPR2/sobel.htm) Compass, (http://homepages.inf.ed.ac.uk/rbf/HIPR2/prewitt.htm) Canny} (http://homepages.inf.ed.ac.uk/rbf/HIPR2/canny.htm) followed by a line detection algorithm from the set {Hough, Convolution, (http://homepages.inf.ed.ac.uk/rbf/HIPR2/linedet.htm) Radon (http://en.wikipedia.org/wiki/Radon_transform) , Cauchy-Crofton (http://en.wikipedia.org/wiki/Crofton_formula) , Fourier} (http://en.wikipedia.org/wiki/Fourier_transform) to detect the illuminated meniscus of the liquid in said transparent containers.

Claim 2: Claim 1 where the transparent containers are illuminated from below.

Claim 3: Flow modulation consisting of multiple valves controlling a multiplicity of inputs and a single output for a multiplicity of containers where the amount of time allotted to opening each valve is varied to modulate the rate of flow through each valve.

Claim 4: The apparatus of claim 3 where the flow modulation for each container is a function of the instantaneous, time-derivative, and/or time-integral of the said container's liquid level.

Claim 5: The apparatus of claim 4 where the flow control parameters are computed by a calibration process consisting of:

1) An output leakage measurement taken by closing all input flow channels and measuring the rate of output flow with all output valves closed.
2) A nominal output flow measurement taken by closing all input flow channels and measuring the rate of output flow with each output valve opened for a specific interval.
3) An input leakage measurement consisting of closing of all output flow channels and measuring the rate of input flow with input valves closed.

4) A nominal input flow measurement taken by closing all output flow channels and measuring the rate of input flow with each input valve opened for a specific interval.

Claim 6: The apparatus of claim 5 where the individual liquid containers are transparent and the rate of flow is measured by the image processing means of line detection.

Claim 7: The apparatus of claim 5 where the rate of flow is measured by detecting any or all of the instantaneous, time-derivative, and/or time-derivative liquid levels of the containers.

Claim 8: The apparatus of claim 5 where one or more pH indicators are added to the containers and a pH value is computed from the reflected and/or absorbed spectra.

Abstract of the Disclosure:

A device to maintain an environment for continuous evolution of micro-organisms or macro-molecules using non-contact sensing means to reduce cost and increase reliability. Precise integrated control over numerous parameters is provided by computer control to allow the range of control necessary to support research environments.

Drawings:
Drawing #1
Thermostat → Turbidostat Cellstat Phagestat Hierarchy

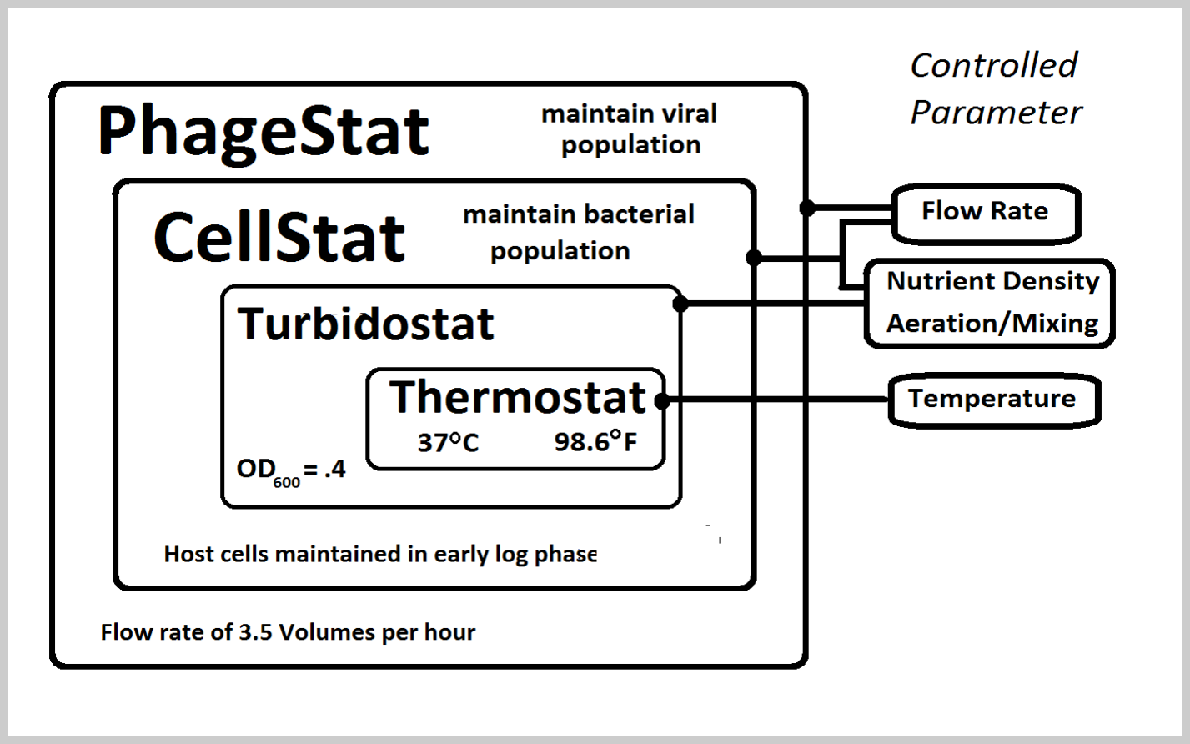
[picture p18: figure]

Drawing #2
Elevation View :

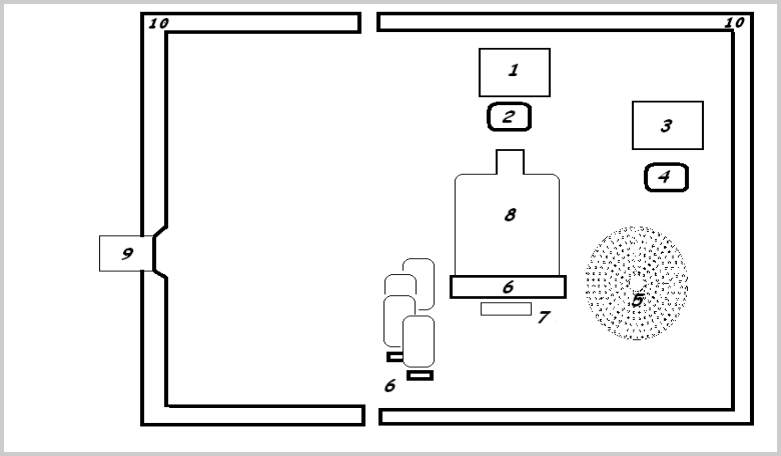
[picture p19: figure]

Keywords: image processing, line detection, controlled illumination, turbidity.

Multi-valve control for liquid flow control of multiple
A Laboratory Apparatus for Macromolecular and Biological Evolution

A micro-controller with 10 digital outputs controlling current sources for LED light sources, pumps, and valves; one pulse-width modulated output controlling a current source; one two-wire (SDA/SCL) interface for a PIR temperature sensor, one analog input for rotary valve position sensing.

10 Digital Outputs:
1. Heater
2. Laser
3. Yellow LED light
4. White LED light
5. Nutrient pump
6. Host cell pump and valve
7. Inducer pump and valve
8. Lagoon outflow pump and valve

1 PWM output: Rotary valve motor

1 Analog input: Rotary valve position sensor

A system for controlling multiple turbidostats and cellstats with minimal medium contact consisting of a dark environmental chamber with an infra-red temperature sensor, a heat source, a multiplicity of light sources under computer control, a digital camera connected to said computer, a multiplicity of liquid pumps, each with a valve whose input and output are in parallel with the pump input and output, an air pump, and stirring means in each of the transparent containers.

A multiplicity of valves each consisting of a stiff rod compressing a soft tube in which the nutrient, cell culture, inducer, or other liquid would otherwise flow freely. A central pointer with adjustable torque which contacts said rods sequentially and flexes them sufficiently to relieve the compression on said tubes allowing liquid to flow freely for a specific time duration. At the end of said duration, the torque being increased to cause the pointer to push past the flexible rod, releasing it to allow it to re-compress said tube, shutting off the liquid flow, whereupon the torque applied to the pointer is immediately reduced to allow the pointer to come into light contact with the rod of the next valve. Said light contact being sufficient for the voltage present on said rod being conveyed to the pointer and then to the analog to digital converter of the computer, allowing the computer to detect the voltage and thereby identify the corresponding valve position of the central pointer.

Image event processing

Image event processing eliminates the need to synchronize lighting changes with image processing or to make special arrangements for technicians to access the apparatus while in use. The controlling computer asynchronously captures images from the apparatus and performs a rapid analysis of the image to determine the lighting conditions. Measurements are made from the image depending upon the lighting conditions as follows:

1. Yellow LEDs lighting the containers from below indicates a level detection event
2. Red laser light projecting a horizontal beam through the host cell container for turbidity measurement
3. Full-spectrum light for images to display on the web page
4. Extremely low light (dark) images indicate integration measurement, summing of pixel values over multiple frames, to detect fluorescence or bioluminescence.
5. Other phage population density indicators may be used and may be detected from the white light image or integrated from multiple full spectrum or monochromatic images.

The image processing loop calculates levels, turbidity, bioluminescence, and visible light color analysis depending upon the lighting detected in the image stream. The lighting control can be implemented by a simple asynchronous mechanism which gives sufficient times to each of the required lighting conditions. During different phases of the experiment, more frequent turbidity or level measurements may be needed and this can be accomplished by changing the lighting schedule.

An important consequence of image event processing is that incorrect readings will not result from a change in light conditions when a researcher opens the capsule during operation. Images acquired from an open device will be interpreted as full spectrum images and used only to update the user monitoring (e.g. Web) image. Previous turbidity or liquid levels will be considered valid until an appropriate image with the correct lighting is acquired.

A single main processor can support multiple phagestat devices as images are captured from each device at various times and are processed to update the monitored parameters according to the following image identification:

1) Fully illuminated image with full color spectrum and normal brightness: Update the human viewable “Web Image.”
2) Moderately illuminated image with predominantly yellow coloration: Identify liquid levels.
3) Low illumination image with predominantly red (laser) coloration: Use intensity measurement and high contrast blob detection to evaluate turbidity.
4) Multiple light sources of different wavelengths, such as red, green, and blue LEDs, behind the primary reactor vessel: Update absorbance data for wavelengths of each point source.
5) No detectable illumination: Add image information to integrated image for bioluminescence detection. For example, we add the value (+green – red/2 – blue/2) for each of 80 images to detect green bioluminescence.

Oath or Declaration:

(required for patent application)

Applicant: Inventor (Peter Brandon Reintjes)

The above-identified application was made or authorized to be made by me.

I believe that I am the original inventor or an original joint inventor of a claimed invention in the application.

I hereby acknowledge that any willful false statement made in this declaration is punishable under 18 U.S.C. 1001 by fine or imprisonment of not more than five (5) years, or both.

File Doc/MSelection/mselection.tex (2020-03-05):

% Template for PLoS
%M13 genes
%I(assembly),
%II(replication init),
%X (DNA accumulation, inside gII) 
%III(fusion),
%IV(assembly),
%V(destabilizing protein),
%VI(minor coat),
%VII(minor coat),
%VIII(major coat),
%IX(minor coat),
%subsubsection is 3rd level heading, PLOS doen't support 4th level.
% Version 3.3 June 2016
% Please follow the template instructions whenever possible.
%
% Once your paper is accepted REMOVE ALL TRACKED CHANGES.
% Use latexdiff to track changes during review to maintain a clean file.
% Visit https://www.ctan.org/pkg/latexdiff?lang=en for info
%
% There are no restrictions on package use within the LaTeX files except that
% no packages listed in the template may be deleted.
% Do not include colors or graphics in the text.
%
% LaTeX source should be a single file: don't use \input, \externaldocument
%
% -- FIGURES AND TABLES
%
% Include table/figure captions directly after paragraph where first cited.
%
% NO GRAPHICS
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
%
% For inline equations, please be sure to include all portions of an equation in the math environment.  For example, x$^2$ is incorrect; this should be formatted as $x^2$ (or $\mathrm{x}^2$ if the romanized font is desired).
%
% Do not include text that is not math in the math environment. For example, CO2 should be written as CO\textsubscript{2} instead of CO$_2$.
%
% Please add line breaks to long display equations when possible in order to fit size of the column. 
%
% For inline equations, please do not include punctuation (commas, etc) within the math environment unless this is part of the equation.
%
% When adding superscript or subscripts outside of brackets/braces, please group using {}.  For example, change "[U(D,E,\gamma)]^2" to "{[U(D,E,\gamma)]}^2". 
%
% Do not use \cal for caligraphic font.  Instead, use \mathcal{}
%
% % % % % % % % % % % % % % % % % % % % % % % % 
%
% Please contact latex@plos.org with any questions.
%
% % % % % % % % % % % % % % % % % % % % % % % %

\documentclass[10pt,letterpaper]{article}
\usepackage[top=0.85in,left=2.75in,footskip=0.75in]{geometry}

% amsmath and amssymb packages, useful for mathematical formulas and symbols
\usepackage{amsmath,amssymb}

% Use adjustwidth environment to exceed column width (see example table in text)
\usepackage{changepage}

% Use Unicode characters when possible
\usepackage[utf8]{inputenc}
%\usepackage[utf8x]{inputenc}

% textcomp package and marvosym package for additional characters
\usepackage{textcomp,marvosym}

% cite package, to clean up citations in the main text. Do not remove.
\usepackage{cite}

% Use nameref to cite supporting information files (see Supporting Information section for more info)
\usepackage{nameref,hyperref}

% line numbers
\usepackage[right]{lineno}

% ligatures disabled
\usepackage{microtype}
\DisableLigatures[f]{encoding = *, family = * }

% color can be used to apply background shading to table cells only
\usepackage[table]{xcolor}

% array package and thick rules for tables
\usepackage{array}

% create "+" rule type for thick vertical lines
\newcolumntype{+}{!{\vrule width 2pt}}

% create \thickcline for thick horizontal lines of variable length
\newlength\savedwidth
\newcommand\thickcline[1]{%
  \noalign{\global\savedwidth\arrayrulewidth\global\arrayrulewidth 2pt}%
  \cline{#1}%
  \noalign{\vskip\arrayrulewidth}%
  \noalign{\global\arrayrulewidth\savedwidth}%
}

% \thickhline command for thick horizontal lines that span the table
\newcommand\thickhline{\noalign{\global\savedwidth\arrayrulewidth\global\arrayrulewidth 2pt}%
\hline
\noalign{\global\arrayrulewidth\savedwidth}}

% Remove comment for double spacing
%\usepackage{setspace} 
%\doublespacing

% Text layout
\raggedright
\setlength{\parindent}{0.5cm}
\textwidth 5.25in 
\textheight 8.75in

% Bold the 'Figure #' in the caption and separate it from the title/caption with a period
% Captions will be left justified
\usepackage[aboveskip=1pt,labelfont=bf,labelsep=period,justification=raggedright,singlelinecheck=off]{caption}
\renewcommand{\figurename}{Fig}

% Use the PLoS provided BiBTeX style
\bibliographystyle{plos2015}

% Remove brackets from numbering in List of References
\makeatletter
\renewcommand{\@biblabel}[1]{\quad#1.}
\makeatother

% Leave date blank
\date{}
% Header and Footer with logo
\usepackage{lastpage,fancyhdr,graphicx}
\usepackage{epstopdf}
\pagestyle{myheadings}
\pagestyle{fancy}
\fancyhf{}
\setlength{\headheight}{27.023pt}
%\lhead{\includegraphics[width=2.0in]{PLOS-submission.eps}}
%\rfoot{\thepage/\pageref{lastpage}}
\renewcommand{\footrule}{\hrule height 2pt \vspace{2mm}}
\fancyheadoffset[L]{2.25in}
\fancyfootoffset[L]{2.25in}
%\lfoot{\sf PLOS}
\lfoot{\sf NCMLS}

%% Include all macros below

\newcommand{\lorem}{{\bf LOREM}}
\newcommand{\ipsum}{{\bf IPSUM}}

%% END MACROS SECTION

\begin{document}
\vspace*{0.2in}

% Title must be 250 characters or less.
\begin{flushleft}
{\Large
\textbf\newline{Mutation Rate as a Selection Mechanism in Continuous Evolution of Bacteriophage} % Title Case
}
\newline
% Insert author names, affiliations and corresponding author email (do not include titles, positions, or degrees).
\\
Peter Reintjes%\textsuperscript{1,2}
\\
\bigskip
\textbf{Innatrix, Inc.}
\bigskip

% Additional author notes using the symbols described below. Insert symbol callouts after author names as necessary.
% 
% Remove or comment out the author notes below if they aren't used.
%
% Primary Equal Contribution Note
%\Yinyang These authors contributed equally to this work.

% Additional Equal Contribution Note
% Also use this double-dagger symbol for special authorship notes, such as senior authorship.
%\ddag These authors also contributed equally to this work.

% Current address notes
%\textcurrency Current Address: Dept/Program/Center, Institution Name, City, State, Country % change symbol to "\textcurrency a" if more than one current address note
% \textcurrency b Insert second current address 
% \textcurrency c Insert third current address

% Deceased author note
%\dag Deceased

% Group/Consortium Author Note
%\textpilcrow Membership list can be found in the Acknowledgments section.

% Use the asterisk to denote corresponding authorship and provide email address in note below.
%* correspondingauthor@institute.edu

\end{flushleft}
% Please keep the abstract below 300 words
\section*{Abstract}
Engineering novel proteins via continuous evolution of bacteriophage currently requires the host bacteria to be transformed with two additional functions: A mutagenesis vector to provide an elevated rate of viral mutation, and a selection mechanism to increase the number of infectious progeny for the individual encoding the improved product\cite{pace}.  I propose using a mutagenesis suppressor as the selection mechanism whereby the desired activity results in a higher number of clones, rewarding the genotype by increasing the number of identical progeny.

% Please keep the Author Summary between 150 and 200 words
% Use first person. PLOS ONE authors please skip this step. 
% Author Summary not valid for PLOS ONE submissions.   
%\section*{Author Summary}
%Lorem ipsum dolor sit amet,

%\linenumbers

% Use "Eq" instead of "Equation" for equation citations.
\section*{Introduction}
Continuous evolution of bacteriophage has the potential to become a potent protein engineering tool\cite{pace}\cite{monsanto}.
Continuous evolution rapidly produces a viral genome containing a gene
which has undergone many generations of mutation and selection for
a particular property.  The generality of this approach to protein engineering
is limited by our ability to insert an expressable initial gene into the phage and create a selection mechanism for the desired activity.

Specifically, the Phage Assisted Continuous Evolution (PACE)\cite{pace} system requires:
\begin{itemize}

\item{}
A modified viral genome replacing a crucial phage gene with the gene to be evolved.

\item{}
A transformed host with inducible mutagenesis.

\item{}
A host plasmid containing a selection mechanism to provide the crucial phage gene in proportion to the desired activity of the evolving gene.
\end{itemize}

\section{M-Selection}
Extremely high, yet controllable, in vivo mutation rates are now possible\cite{mutation}.  This broad-spectrum mutagenesis with a (claimed) 320,000:1 dynamic range is generated and can be controlled within an individual host cell.  I suggest that if this mutagenesis is initiated  by infection, say with the phage shock promotor but then reduced by the desired activity, the two principal components of evolution will be satisfied: The desired activity will be selected for as the number of phage progeny of the individual exhibiting that activity will be amplified by more faithful reproduction.  I propose calling this mechanism Mutagenesis-selection or M-selection.  So far, all PACE-derived procedures induce a uniform mutagenesis in the lagoon: M-selection doesn't even require the small-molecule (Ara) induction mechanism.

We require 2 clones per generation to infect hosts and produce phage to prevent washout of a genotype. Assuming phage production of 100/hour and a lagoon transit time of one hour, we calculate calculate a mutation rate of about 4 mutations per phage genome.  The percentage of phage progeny which are exact copies of the parent is given by the Poisson distribution where $\mu = 0$ is the expected number of mutations and $\lambda$ is the mutation rate per virion (mutation rate/base * 6kbp/ genome).
A mutation rate of $\lambda = 4$ gives a 1.8\% probability of zero mutations.
\vskip 0.2cm
\begin{eqnarray}
\label{eq:POC}
\mathrm{P}\left( \mu, \lambda \right) = \frac{{e^{ - \lambda } \lambda ^ \mu }}{{\mu!}}
 \rightarrow P(0,4) = \frac{{e^{ - 4 }}}{{1}} = .018
\end{eqnarray}

So the maximum per-base mutation rate that a genome could tolerate and still stay in the lagoon is $6400/4 = 6.25 X 10^-4$.
Liu et al. claim 322,000 times basal mutation rate. Basal rate is possibly ambiguous here if they are referring to the basal rate of E. coli producing E. coli  ($4x10-10$) vs. E coli producing M13 phage ($7.2 x 10-7$), but in either case their claimed dynamic range covers the required phage mutation crossover rate required to avoid washout.

PACE is designed to keep the transit time of host cells through the lagoon on the order of one generation.  However, at very high levels of mutation it seems unlikely that succeeding generations of E. coli mutants or phage will remain viable. Furthermore, the continuous flow environment ensures that there can be no other selection mechanism beyond the number of faithful copies of a particular genome.  The obvious exception to this would be a colony or biofilm which remains somehow attached in the lagoon, but the population size for such entities would be limited by the surface areas within the lagoon, and not the volume.

Taking a phage production average of 100/hour for normal M13 infection requires us to have a cloning rate of at least 2\%: two faithful copies per infection in order to avoid washout.  The previous consideration of high mutation rates would seem to allow slower flow rates, which will lower this minimum fraction.

An important difference with PACE is that mutagenesis is not induced externally and therefore in uninfected cells, so there may be a minimum number of faithful copies produced before the mutagenesis products are expressed by the infected host.  It may prove useful to retain the arabinose-induced mutagenesis as a way of achieving a baseline mutation rate in the lagoon, or an ante-chamber for the lagoon where induction can begin before exposure to phage.

As the evolving protein approaches a high level of desired activity, the proportionally lowered mutation rate will ensure that more viral progeny contain exact copies of the parent genotype, while a baseline mutation rate ensures that our mechanism to lower the mutation rate will not result in stagnation.

A possible drawback to this technique is that the mutation space is less agressively searched as the desired activity improves.  But there is no particular reason that the modulation of mutation rate necessary to produce the population shift will be a particularly low (e.g. natural) mutation rate.

\section{Possible Benefits of M-Selection}
\begin{enumerate}
\item{The virus is not crippled, that is, no critical genes are removed from the virion which should improve our ability to propagate phage prior to the evolution experiment.  Care must be taken to ensure that the evolving gene is not discarded, but M13 plus one additional gene or domain is exactly what has been perfected in phage display.}
\item{No phage genes are required in a host plasmid.  This avoids the problem associated with the presence of gIII in the host.}
\item{High rates of mutation will be associated with individuals exhibiting little or none of the desired activity, and these lines of descent (both E. coli and phage) will be subject to catastrophic levels of mutation and low viability. This may reduce the importance of a carefully controlled flow rate.}
\item{Clonal Interference\cite{dynamics}, the inabiltiy of a single genotype to gain sufficient advantage to become fixed in a population due to weak selection pressure is viewed as a problem in experimental evolution (one mutant has an important beneficial mutation, but also has a bad mutation hitch-hiking along which attenuates the advantage as compared to a sibling with neither mutation. In our case, maybe not a disadvantage as it keeps variety in the lagoon. Multiple genotypes in the lagoon at sample time would be informative. Does weak selection correspond to a flatter fitness landscape? I'm making an assumption here that M-selection corresponds to what Drake and others refer to as 'weak selection'.}

\item{We get 'genetic drift' for free, or at the cost of defective interference, anyway. To quote Patent \#9023549 (Havard/PACE):
\quote{\textit{A major problem with traditional directed evolution, whether in vitro or in vivo, is that libraries that do not contain any functional variants will be entirely lost, and the effort wasted--even if functionality lies only a couple of mutations away. The present invention overcomes this problem by allowing "switchable" genetic drift. This can be achieved by, for example, providing "free" propagation components to all library members, such as by inducible expression from an anhydrotetracycline-regulated titratable promoter, enabling all variants to infect host cells. By providing enough "free" propagation components, but less than the optimal level, any functional variants that arise will produce slightly more of the missing propagation components, produce more infectious progeny, and take over the population. }}}

\item{Adding a negative selection component may be simpler than in PACE: Just need something to re-up-modulate the mutation rate as a result of off-target binding. A suppressor supressor?}

\end{enumerate}

The nominal (high) mutation rate can be chosen to guarantee that there will be a minimum number of non-mutant copies produced for every infection.  This percentage (of clones) will then increase proportunally as the mutation rate is reduced.

The downside to this is defective interference from all the propagating mutants with none of the desired activity. So they are infecting host cells and crowding out the 'nice clones' as we wait for their lineages to undergo Error Catastrophe.  It would be good to know how many uninfected host are making it through the lagoon. If we have an excess of uninfected host, this would reduce defective interference.

In the first generation, even a fatal mutation will be packaged in a viable virion, so that it will infect a host cell. But it will go no further if the fatal mutation results in non-functional coat proteins, origin of replication, packaging signal, or whatever. So in the worst case, a fatal mutation results in the production of 100 dead-end virions.

The maximum mutation rate will be experienced by phage that have none of the desired activity and we want this rate to ensure that the accumulation of 5 non-beneficial mutations will result in a fatality.  The growth of a defectively interfering population is thus limited to 100^5, 10^6.  This number is reached only if for phage that has accumulated four non-beneficial, non-fatal mutations.  Presumably these are silent mutations as the phage genome is minimal and highly conserved. We should also recognize that a reversion to wild-type phage (shedding the payload gene), will also subject the phage to maxiumum mutation in every generation.

Beneficial mutations resulting in detection of the desired activity will reduce the mutation rate, resulting in more cloned phage, which will inherent this ability to supress the mutation rate.

Even if it is possible to have a series of mutations which result in a viable phage after ten generations, this genotype will not.  For the high-mutation
all of the different mutations that occur in these 10 generations would have to be non fatal. resulting in 10^10 viable phage mutations.

For a given maximal mutation rate, what are the
Can we estimate a probability for M13s resistance to mutation.
Since different types of organisms, and even individual species, have some control over their exposure to mutations.

Perfect replication okay for Artificial Selection

There is at least one aspect of natural evolution which we do not have to replicate in directed evolution.  The principals of evolution make it clear that perfect DNA replication is a recipe for extinction in any environment that is subject to change.  But we are clearly going to engineer our continuous evolution environment to be as stable as possible, so future experiments can take advantage of DNA replication and repair mechanisms to allow for perfect replication at the upper end of the usable range.

Phage has a higher natural mutation rate than all types of cells, but our artificial environment does not have to respect
There is no reason not to utilize the entire range from Mutation Storm to Perfect Replication.  In fact, modifications which can achieve perfect replication.

So we may do something nature never did, which is bring all the tools of replicative fidelity to phage reproduction.

What fraction of the M13 gene can carry non-fatal mutations. Including all the silent mutations, plus those which represent similar amino acid substitutions,

\begin{minipage}{\textwidth}
Figure 1 shows the combined mutagenic/selection mechanism replacing the Mutagenesis Plasmid(MP) and Accessory Plasmid (AP) in PACE.

\def\boxone#1{
  \put(19,30){\line(1,0){67}}     % horiz top
  \put(19,0){\line(1,0){67}}      % horiz bottom
  \put(20,0){\line(0,1){30}}      % vert left
  \put(85,0){\line(0,1){30}}      % vert right
  \put(25,15){#1}
}
\def\boxtwo#1#2{
  \put(19,30){\line(1,0){80}}     % horiz top
  \put(19,0){\line(1,0){80}}      % horiz bottom
  \put(20,0){\line(0,1){30}}      % vert left
  \put(98,0){\line(0,1){30}}      % vert right
  \put(25,17){#1}
  \put(25,7){#2}
}
\def\circleone#1#2{\circle{#1}\put(-17,-4){#2}}
\def\circletwo#1#2#3{\circle{#1}\put(-17,0){#2}\put(-15,20){#3}}

\picture(400,150)(-90,0)

\put(90,90){\vector(0,-1){12}}
\put(90,56){\vector(0,-1){26}}

\linethickness{2pt}
\thicklines
\put(0,15){\circleone{40}{\Large{\ \ P1}}}
\put(0,35){\vector(0,1){16}}
\put(10,40){\small Protein}
\put(20,15){\vector(1,0){34}}
\put(25,18){DNA}

\put(35,90){\boxtwo{\ Phage Shock}{\ \ \ Promoter}}
\put(-20,62){
\fbox{%
    \begin{minipage}{1.0in}
Activity Induced\linebreak
\hspace*{5 mm}Repressor
    \end{minipage}%
}}
\put(64,70){\vector(1,0){18}}
\put(83,65){\fbox{\begin{minipage}{0.05in}
		\hfill\vspace{0.20in}
            \end{minipage}
           }}
\put(35,0){\boxtwo{\ \ Mutagenic}{\ \ Components}}

\put(134,15){\vector(1,0){26}}
\put(180,15){\circleone{40}{\Large{\ \ F1}}}

\endpicture
\vskip 1.0cm
\centerline{\bf Fig 1. M-selection Plasmid}
\end{minipage}
\vskip 0.2cm

\section{Comparison with Natural Selection}
Selection pressure for an optimal mutation rate has its own natural history\cite{evomut} although for settled phyla we see consistent\cite{drake91}, low mutation rates.  Bacteriophage $6.4 X 10^-4$, and multicellular eukaryote mutation rates are higher than bacteria $4 X 10^-11$ and single cell eukaryotes $3 X 10^-10$.

A selection mechanism for lowered mutation rate would not seem to correspond to anything in the natural world.  Natural selection is largely about responses to the external environment, which we control closely in laboratory evolution.  Perhaps the closest parallel is found in species which can reproduce by asexual or sexual reproduction and change the rates between the alternatives as a way of accessing more diversity through sexual reproduction or producing more clones via asexual reproduction.

\section*{Comparison with Sexual/Asexual Reproduction}
Sexual reproduction is not the same as an elevated mutation rate, but it shares the characteristic that even a perfectly fit individual will not be producing faithful copies of its genome. For organisms with access to both forms, the percentage of offspring produced by asexual reproduction would be comparable to our percentage of true copies.
\subsection*{Yeast}
Although yeast has access to both sexual and asexual reproduction, the time and energy cost of sexual reproduction is high and it is generally induced by stress, indicating a need for more genetic diversity.
\subsection*{Daphnia} 
In Daphnia, longevity and healthy survival to the end of the season result in so-called ``winter eggs'' which reproduce asexually, providing a percentage of offspring which are clones of the parent. The cost differential between sexual and asexual reproduction is low and each generation represents a mix of both.

\section*{Materials and Methods}

\subsection*{Population Dyamics of Bacteriophage (Under Construction)}
\subsubsection*{Clones versus Mutants}
Although it may sounds like the title of a bad sci-fi movie, this precisely states the selection mechanism of mutation.
\newline
Percentage of activated genes due to Phage Shock promoter.
\newline
Number of polIII-(mutagenic polymerase) transcripts times error rate due to mutagenic polymerase.
\newline
Error rate of normal polII, polIII?
\newline
Number of phage particles produced np(0-6 min) = 0 (six minutes before any phage appears), then production between 75-200 per hour.
\newline
Some initial single-strand (virion) DNA production will occur in non-mutagenic environment, then mutants appear, until suppression of mutagenesis due to binding (e.g. the desired activity).

% Results and Discussion can be combined.
\section*{Results}
.jpg}
\newline
M13 with 0.0 cAMP + MP6 $10^-7$
.jpg}
\newline
M13 with 5 milliMolar cAMP + MP6 $10^-5$
.jpg}
\newline
M13 with 50 milliMolar cAMP + MP6 $10^-5$

\subsection{Methods for Lowering the Mutation Rate}
\subsubsection*{RNA Anti-sense}

The components for the broad-spectrum, high-level mutagenisis described in Badran and Liu\cite{mutation} are variations (often single mutation variants) of the functional domains of high-fidelity DNA replication, and as such are not suitable targets for RNA anti-sense interference. Any such anti-sense interference would be likely to affect their normal counterparts which are needed for faithful reproduction.

RNA anti-sense of gIV could be utilized to block the phage shock promotor which is the primary stimulus that activates mutagenesis.

\subsubsection*{Other Methods}
\begin{itemize}
	\item Suppress pIV production or otherwise block phage shock promotor.
	\item Selectively block downstream components of mutagenesis.
	\item Enhance production of wild-type high-fidelity replication components.
\end{itemize}

%\section*{Discussion}
%Modeling needs work.
%\section*{Conclusion}
%
%I think this will work.
%\section*{Supporting Information}

% Include only the SI item label in the paragraph heading. Use the \nameref{label} command to cite SI items in the text.
%\paragraph*{S1 Fig.}
%\label{S1_Fig}
%{\bf Bold the title sentence.} Add descriptive text after the title of the item (optional).

%\paragraph*{S1 Appendix.}
%\label{S1_Appendix}
%{\bf Algorithm.} The code goes here.

%\paragraph*{S1 Table.}
%\label{S1_Table}
%{\bf Graph maybe.} The Graph goes here.

%\section*{Acknowledgments}
%So many people to thank.

\nolinenumbers

% Alternative to directly entering bibtex entries:
% 1) Compile BiBTeX database using plos2015.bst style file
% 2) Paste the contents of your .bbl file here.
\begin{thebibliography}{10}

\bibitem{pace}
Esvelt K. M., Carlson J. C. \& Liu D. R.
\newblock \textit{A system for the continuous directed evolution of biomolecules}.
\newblock Nature 472, 499–503 (2011).

\bibitem{mutation}
Badran AH, Liu DR.
\newblock \textit{{D}evelopment of potent in vivo mutagenesis plasmids with broad mutational spectra}.
\newblock Nature Communications. 2015;6:8425. doi:10.1038/ncomms9425.

\bibitem{dynamics}
Barrick, Jeffrey E., Lenski, Richard E.
\newblock \textit{{G}enome Dynamics during Experimental Evolution}
\newblock  Nat Rev Genet, 2013 December, 14(12), pp. 827-839, doi:10.1038/nrg3564

\bibitem{evomut}
Lynch M.
\newblock \textit{{E}volution of the Mutation Rate}.
\newblock Trends in Genetics, 2010 August; 26(8): 345–352. doi:10.1016/j.tig.2010.05.003.

\bibitem{monsanto}
  Badran A. H., Guzov V.M., Huai Q., Kemp M. M.,Vishwanath P.,Kain W., Evdokimov A., Moshiri F., Turner K.H.P., Malvar T., Liu D.R.
  \newblock \textit{{C}ontinuous evolution of Bacillus thuringiensis toxins overcomes insect resistance.}
  \newblock  Nature 533,58-63 (2016) doi:10.1038/nature17938.

\bibitem{drake91}
  Drake J. W., 
  \newblock \textit{{A} constant rate of spontaneous mutation in DNA-based microbes}, 
  \newblock  Proc Natl Acad Sci U S A. 1991 Aug 15;88(16):7160-4.

\bibitem{domingo2009}
  Domingo-Calap P, Cuevas JM, Sanjua´n R (2009)
\newblock The Fitness Effects of Random Mutations in Single-Stranded DNA and RNA Bacteriophages.
\newblock PLoS Genet 5(11): e1000742. doi:10.1371/journal.pgen.1000742

\end{thebibliography}

\fbox{\begin{minipage}{4.0in}
Bacteriophage M13. The genome size is 6407 bp (4). The
mutational target is 258 bp of an inserted Escherichia coli
lacZa sequence (5). The spontaneous mutant frequency is $6.4 x 10-4$ per genome or $7.2 x 10-7$ per base pair \textit{Drake, 1991}
\end{minipage}}

\end{document}

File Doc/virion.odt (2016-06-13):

Some ideas for

Engineering the Virion

"The Power of Negative Thinking"

Peter Reintjes 5/24/2016

PACE 2.0 introduced Negative Selection to deal with the issue that better binding might simply broaden the range of targets and not make a protein more specific for a particular target. Negative selection against similar targets is a way to gain specificity as well as binding.

Ref: Negative selection and stringency modulation in phage-assisted continuous evolution. Carlson, et al.. Nature, Chemical biology Feb 2014

A smaller genome is highly advantageous to phage (shorter life cycle, lower energy budget, more virions). This deletion of unneeded genes has been a major problem! Genes for anything consistently produced by E. coli will be eliminated from the viral genome. Seems like a problem we can turn into a tool. Here's a possibility:

1) Use only negative selection mechanism (take pIII out of the host Bait plasmid).

2) Put pIII back into phage along with hybrid(Predator), the target binding now being necessary to make the conditions right for a functional pIII.

3) Our new positive selection mechanism is one that generates pIII inhibitor by default and is shut down by desired Predator/Bait binding. This binding turns-off default 'pIII poisoning' (or other anti-viral/negative-selection mechanism).

'By default' can be improved to 'by default, after infection' using the phage shock promoter.

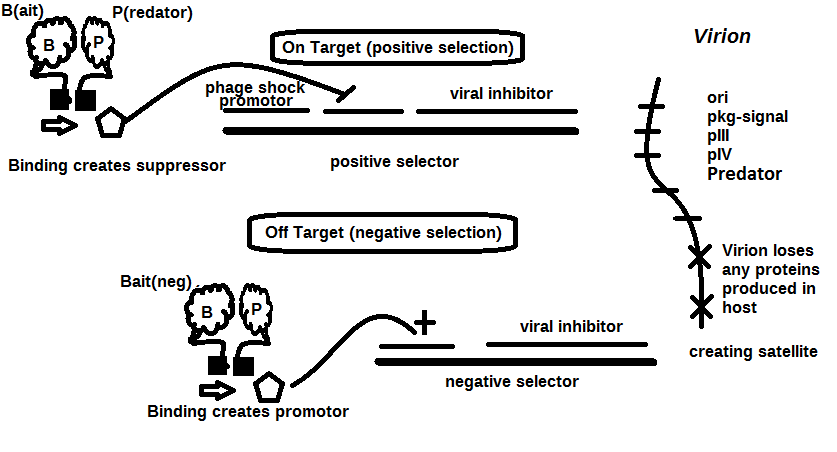
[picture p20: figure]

This could not only work, but I think it gets better:

4) Program E. coli (plasmid, genome pro-phage, or pre-infect with “helper-phage” [but no pIII - so no infection response and no pIV which triggers phage shock protein]) to produce most viral proteins by default -- not strictly necessary for the idea above, but may help on the front of keeping the phage from discarding the genes we want by having a near-minimal viral genome (at some point, we will stop calling this construct a phage. It will be more like a satellite).

Having a larger code space in the phage at our disposal will allow us to play with larger proteins – I’m not certain, but I think the physical size of filamentous phage is a kind of thermodynamic restriction, some trade off with the adhesion of the coat protein, possibly. But turning our phage into a minimal satellite (~3 genes + signaling DNA) might allow us to work with larger proteins than anyone else.

We will of course have all the power of multiple negative selection targets to also turn on production of inhibitor, and with the new approach, we can concentrate on the more general purpose negative-selection cassette design, with the idea that a given experiment will use one of these negative selection targets in 'default on' mode, to provide the positive selection.

Working with a large protein, there’s nothing to keep the phage from discarding the sequence for domains that aren’t involved with target binding, unfortunately, this is fundamental to PACE, you may just end up with a few domains of your original protein plus the important hybrid section. The absence of these domains would mean there is nothing to bind with the negative-selection bait and therefore no inhibitor will be created – so the absence of a domain of interest will be indistinguishable from a mutated domain evolved away from binding with the negative selection mechanism (the latter being the thing we wanted). If we truly want to evolve away from some activity – like eliminating a side-effect in a therapeutic, the active site must be the same as the one participating directly in the positive selection binding – The positive selection working to keep it in the phage genome and the negative selection keeping it from binding with a particular (unwanted) target.

Since the positive selector is really a ‘default on’ inhibitor, we can have more than one positive selector and when all of them are activated we get minimal inhibitor production. This could preserve important parts of a large protein in an environment that is trying to strip everything down (I’m not going to pretend that the mechanics of this is easy, finding multiple targets for different parts of a large protein, or how different binding sites of a large protein will still bring the other half of the hybrid into the right position, just saying it might be possible). I’m not even trying to make this fit a specific mechanism like bringing two pieces of acyclase together as the ‘binding signal’.

Can we create multiple (somewhat independent) positive selection mechanisms which can each maintain part of a complex protein in the viral genome? The presence of all of them being necessary to maintain the entire sequence, but allowing for (at least one) of them to improve fitness through improved binding.

This suggests two different kinds of positive selector:

1. Modulated response to improve the binding of the particular domain of interest – this is the original positive selection. By controlling the amount of functional pIII, or slowing down any of the processes leading up to phage release. Slowing down phage release could be particularly effective as this is a continuous flow system and hosts are continually washing out.
2. Go-noGo which requires the presence of the domain to be maintained. A phage missing a required domain is eliminated – we can interfere with release or poison a coat protein. How can we guarantee the presence of a particular sequence/protein?

One result of multiple positive/negative selectors could be many 'neutral' mutations which slightly improve one while equally diminishing another. This might motivate adjusting the mutation rate down – though probably not down to the limit of one mutation/phage.

For evolution we need a modulated response from the negative selection. The 2014 paper on PACE+negative selection emphasizes this modulated characteristic of ‘pIII poisoning’, so this will be desired of any alternative inhibitor, though we may find a use for a crude 'instant-death' inhibitor as in the Go-NoGo positive selector used to maintain the phage genome.

The most pressing example of this need for a modulated response (since we are now perversely using a negative selection mechanism for positive selection) is the case of late infection, where some of the pIII inhibitor may have been created in the host before the virus gets there. This could be mitigated if the so-called 'default' production of pIII inhibitor is triggered by infection (PS) instead of building up the anti-pIII while waiting for the virus. Now that the virus once again contains its pIII gene, triggering on infection is a nice large signal input without even the possibility of leakage.

I realize it must sound completely crazy to put the pIII back into the phage: and I'm not suggesting it just to get around the Harvard patent (which it may or may not even do, but is something to be considered -- we'll have to see when a patent around the negative selection idea appears), but this seems like a much bigger playground than the idea of having pIII in the host.

Two positives are that it seems easier to modulate inhibitors than pIII production, and these inhibitors won't affect infectability (at least the early stages of infection), or can be made to be dormant prior to infection.

When M13 was mutated to reduce its number of DNA bases (from 6.4 knt to 221 nt), then the number of p8 copies was decreased to fewer than 100, causing the p8 coat to shrink in order to fit the reduced genome. The phage appear to be limited at approximately twice the natural DNA content. However, deletion of a phage protein (p3) prevents full escape from the host E. coli, and phage that are 10-20X the normal length with several copies of the phage genome can be seen shedding from the E. coli host.

Reference for the idea of minimal size for DNA bacteriophage:

1) Specthrie, L; Bullitt, E; Horiuchi, K; Model, P; Russel, M; Makowski, L (1992). "Construction of a microphage variant of filamentous bacteriophage.". Journal of Molecular Biology 228 (3): 720–4. doi:10.1016/0022-2836(92)90858-h. PMID 1469710.

Anti-viral modulators

Today, "anti-viral" technology is really about human/animal viruses, so maybe this is more of an analogy than literal. But since we clearly aren't trying to prevent infection, the early-stage viral intervention ideas are of no use, only the later ones.

We will not be restricted to "pIII poisoning" as the only inhibitor, here is a list of anti-viral intervention points as a starting point to discuss inhibitor design. Viral inhibition points that are too early (e.g. prevent infection) are crossed out.

Slowing metabolism of the host is the ultimate anti-viral

Anything that slows down the host can be considered anti-viral for our purposes. After all, we're not trying to 'cure' the E. coli of it's infection, just reduce the number and/or unfectiousness of virions released into the lagoon. This really broadens the idea of an inhibitor and might be easier than other anti-viral approaches, since we can even kill the patient, if needed. It may be hard to keep this in mind; The needed inhibitors are just anti-viral-propagation, and not necessarily pro-host.

To use a system where a significant amount of the inhibitor may be present in the early stages, we will probably want to ramp up the flow rate, starting from a near stagnant lagoon (where slow growing things can fester) to a PACE-like flow rate that washes out the slowest-growing, inhibited E. coli, maybe even before they release any phage. Linking total inhibitor concentration to bio-luminescence would be useful for us to control the flow rate and it should be dead easy – simply producing LuxA/B (after phage shock) will cause luminescence to correlate with metabolic rate – the very thing affected by our inhibitors.

This has been leading me to think about the bacteria+temperate-phage as an organism that receives an infectious satellite from a previous generation, tests it for a particular property while creating modified versions and then releases the new satellites in proportion to how well the tested property led to the reduction of an inhibitor. Anything which slows release of the new infectious particles is a potential inhibitor. An agent which increased the rate of production of the viral particles would be a positive selector. If the inhibition is acting on the bacterial metabolism, the phage/satellite cannot easily mutate to get around it – it can only mutate something that will shut off the inhibitor – and of course, that is the easy path we've given it for its evolution. It may come up with a novel way of shutting off the inhibitor. But that kind of novelty is reserved for Evolution (with a big E), instead of the tinkering that we are doing (is that a valid distinction?).

What I’m really trying to do is broaden the potential mechanisms to anything that reduces the

number of released phage particles, (yes they are phage inhibitors, but really we can do any number of things to the E. coli to get less phage production, no?) Think of all the things that might do this, affecting any mechanisms in the E. coli that would slow it down – or rather slow anything that leads to particle release. Attacking the transcription/expression mechanisms (we don’t care about future generations of this particular E. coli). There are many things that have nothing to do with the genes left in the phage/satellite, and so reduce the chances of an alternative evolutionary ‘escape’.

Steve: I think that sculpting expression of an inhibitor such that phage production runs from just above wash out to full production based on the two hybrid strength will be tricky and time consuming.

To help with this, I suggest ramping the flow rate from near zero to full flow rate based upon

Lux feedback. Where lux is a measure of the metabolic performance of infected E. coli, as a proxy for phage release.

1) Un-infected E. coli produce low lux levels,

2) E. coli infected with a phage that doesn’t have a good binding produces lux slowly. E. coli is crippled by Phage Shock triggered inhibitor that isn’t suppressed by good Preditor/Bait binding.

3) E. coli infected by phage that successfully suppresses inhibitor produces lux according to

its ‘health’.

Your thesis presumes that it would be facile to create phage inhibitors. Of the possible mechanisms you list near the end, I think antisense, and possibly the expression of negative interfering versions of the capsid protein might qualify to be facile enough.

In the case of antisense, if it's a large antisense transcript, it might be hard for the virus to evolve around it. So maybe that could be done in a straight forward way. If it was a short antisense transcript, the virus could evolve around it. It would be possible, as you suggest, to offload the target transcript into some plasmid or other form for host expression. Then the target of the inhibition would be replenished with the host, preventing mutagenesis of the target from becoming a factor.

Off loading phage proteins onto plasmids may be tougher than you're imagining. The problem is that that the complementing plasmid will be unstable. Using phage shock promoters to try to keep expression off till needed seems like a good solution to that.

Steve Hardies: I think trying to offload very large numbers of phage proteins to host expression would be almost impossible. You'd be tied up forever trying to replace all the promoters with phage shock promoters and getting the relative expression right. People always use M13 helpers for that sort of

purpose, because growth of the helper as an M13 provides selection to keep the genes. But you'd have to make it a gpIII- helper, and either make it immune to the hybrid modulated inhibition, or provide some complicated system to constantly feed helper into the lagoon. Seems complicated.

Before cell entry

Entry inhibitor

Uncoating inhibitor

During viral synthesis

Reverse transcription

Integrase

Transcription

Translation/antisense ??

Translation/ribozymes ??

Protein processing and targeting

Protease inhibitors

Assembly

Release phase

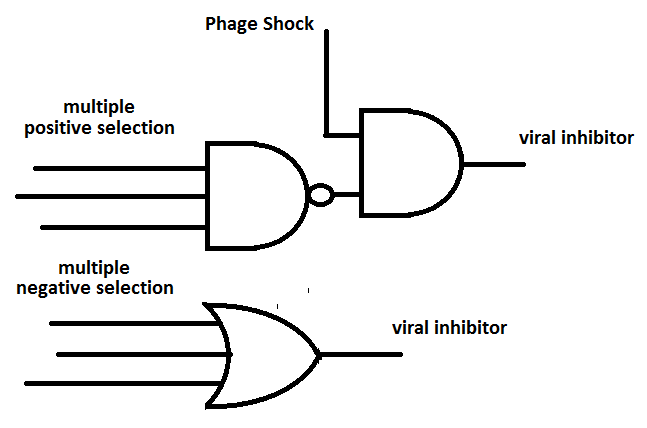
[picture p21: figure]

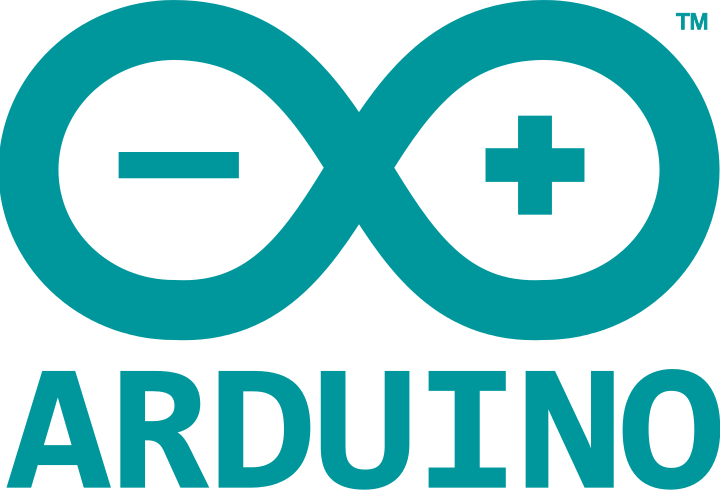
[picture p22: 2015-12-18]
Doc/Arduino.png

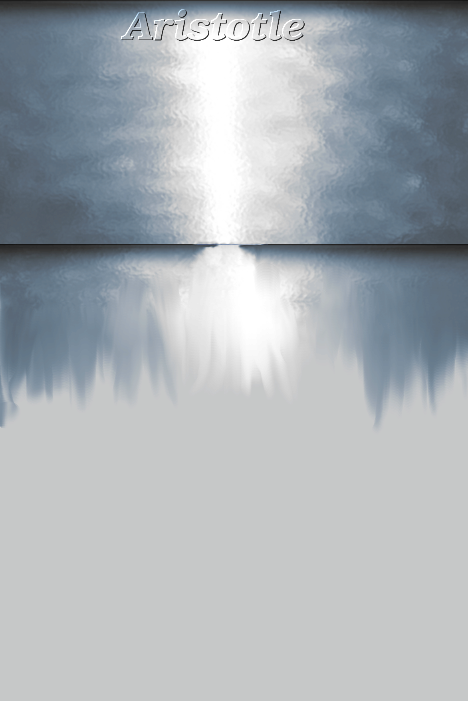
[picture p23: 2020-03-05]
web/images/aristotle.png

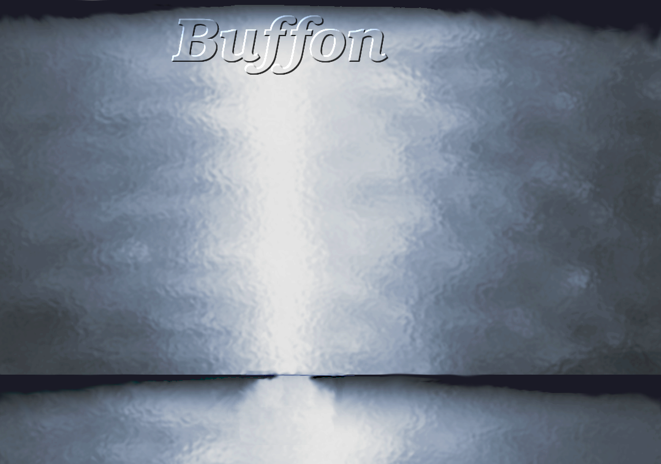
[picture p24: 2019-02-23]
web/images/buffon.png

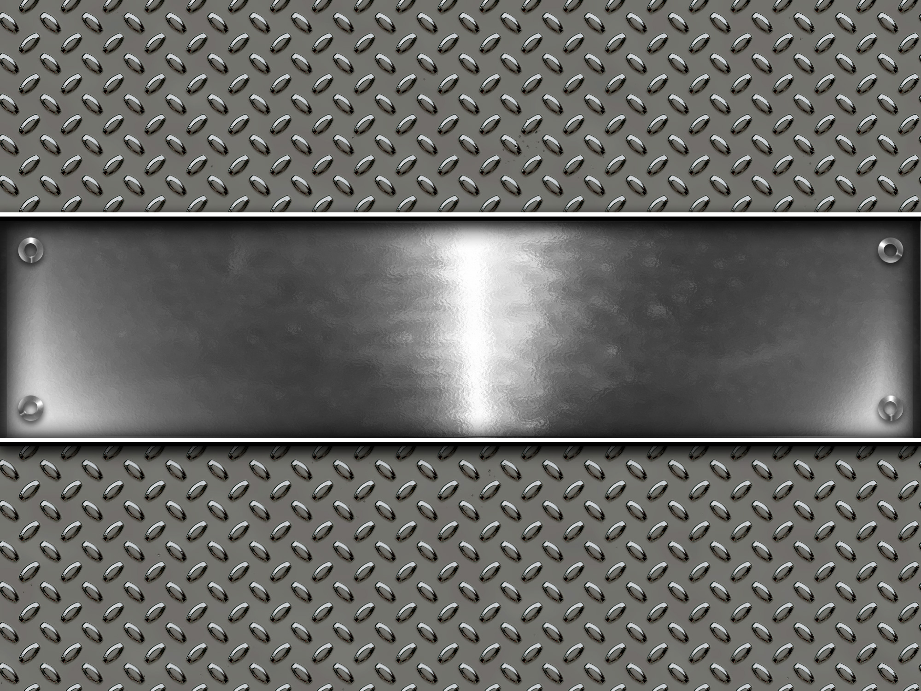
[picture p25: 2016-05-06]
web/images/nameplate.jpg

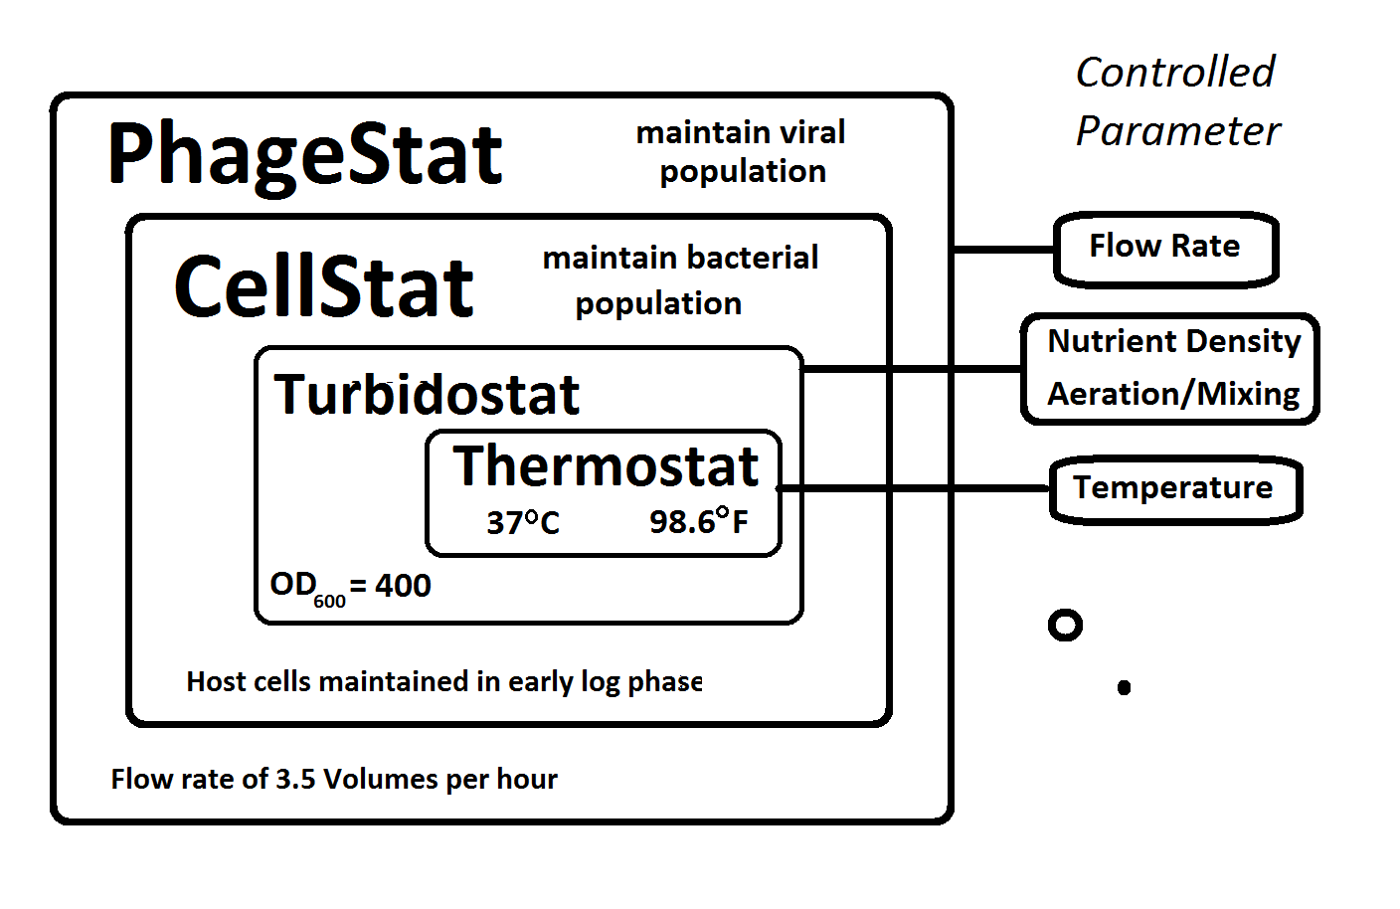
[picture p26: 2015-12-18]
Doc/PhageStatHier2.png

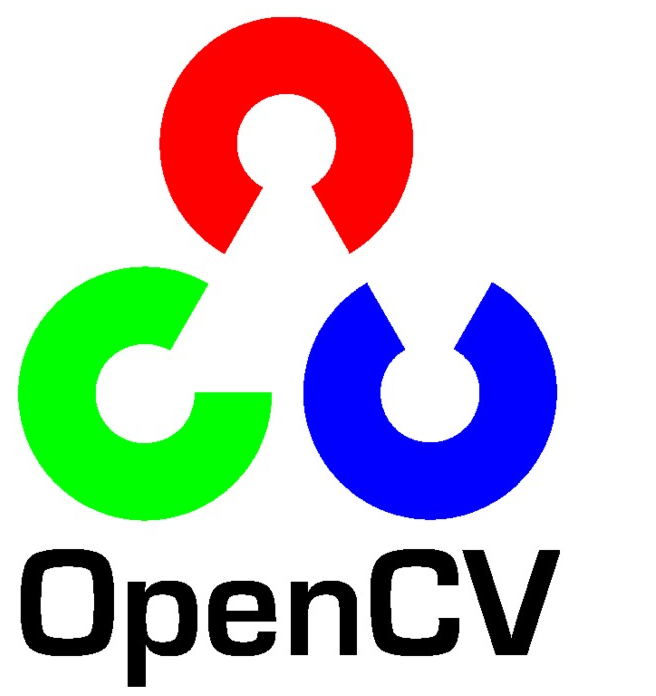
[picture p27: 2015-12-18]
Doc/opencv.png

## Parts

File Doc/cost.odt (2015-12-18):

Cost per Processing Unit

Cost Processor Programming Language

$500 Desktop PC Python/C++

$35 Raspberry Pi Python/C++

$10 Arduino C++

$0.40 PIC 12C509A C

37.5 np† E. coli (Harvard) DNA

1.25 np† E. coli (Innatrix) DNA

† np = 10⁻¹¹ dollars (e.g. nano-pennies)

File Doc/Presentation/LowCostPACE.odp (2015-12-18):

## “Evolution as a Tool”

Phage Assisted

Continuous Evolution

...on a budget

## Overview

- PACE (Esvelt et. al. Nature, April 2011 )
- Use a virus to evolve a custom protein
- Off the shelf hardware for only $30K
  - or -
- Open-source Hardware/Software ~$1000

## Innatrix Motivation #1

- Shigella kills 1,000,000 people per year, mostly children in the developing world
- Shigella without the proteases Pic and SepA is harmless
- Hypotheses: Protease inhibiters with strong binding affinity to Pic and SepA would short-circuit Shigella's virulence
- Hypotheses: Such proteins added to LactoBacillus or other probiotic could provide inexpensive, long-term immunity

## Technology Potential

- Protein binding affinity is the principal characteristic of metabolic processes and pharmaceuticals
- Higher binding affinity would lower dosage for any protein therapeutic
- Large protein molecules will have reduced side-effect potential of small-molecule pharmaceuticals which easily cross metabolic barriers and have more interaction potential
- Proteins degrade quickly in waste stream
- Proteins can be easily metabolized without stressing renal function

## PACE: Phage Assisted Continuous Evolution

- Bacterial virus (M13) evolves the protein
- Virus replicates inside E. coli
- Increase mutation rate by a factor of 100
- E. coli rewards improvements by providing a protein that increases viral infection.

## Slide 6

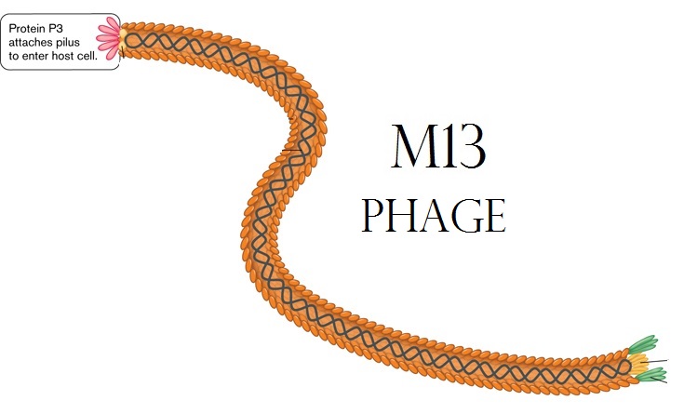
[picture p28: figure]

## PACE: Phage Assisted Continuous Evolution

- M13 virus (phage) but substitute a sequence of the protein to evolve for its fusion gene.
- E. coli with two extra plasmids (chromosomes)
  - Mutation: Arabinose activated mutagenesis
    (error-prone DNA polymerase)
  - Selection: M13 'fusion' gene activated by
    a particular protein interaction
  - E. coli host cells flow through “lagoons”
  containing populations of evolving viruses

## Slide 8

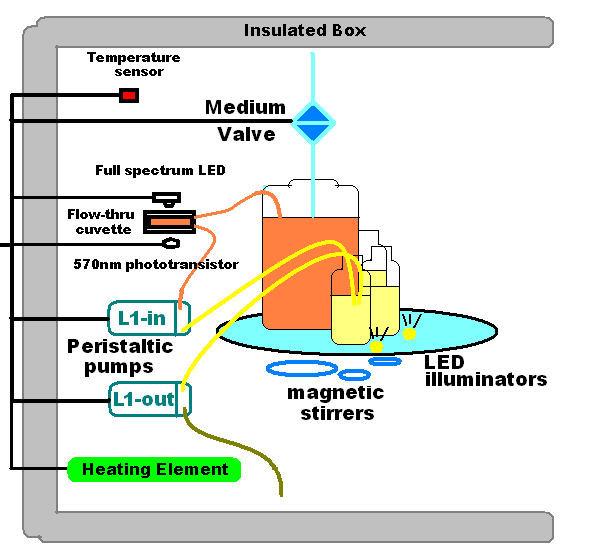
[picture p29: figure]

## Principal Ideas

- Virus life cycle is shorter than E. coli
- No Arabinose in E. coli hatchery (no mutation)
- E. coli pass through lagoons containing Arabinose in less than one generation
  (e. g. not enough time to create E. coli mutants)
- Several phage generations occur during the flow-through time of the lagoon
- Different kinds of interaction can trigger production of the 'infection' protein

## Turbidostat version 1.0

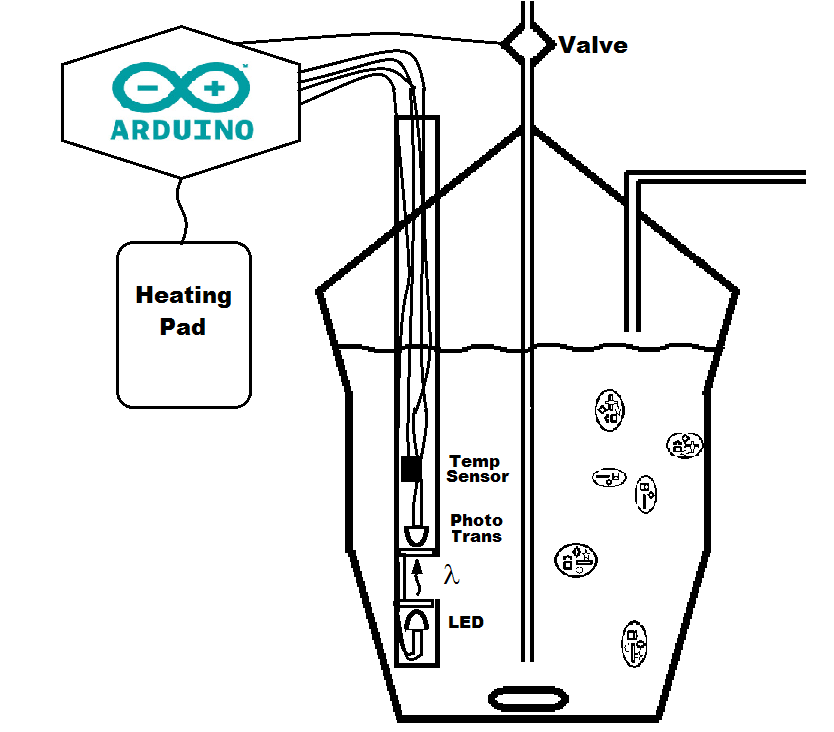
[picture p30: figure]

## Non-contact level-sensing

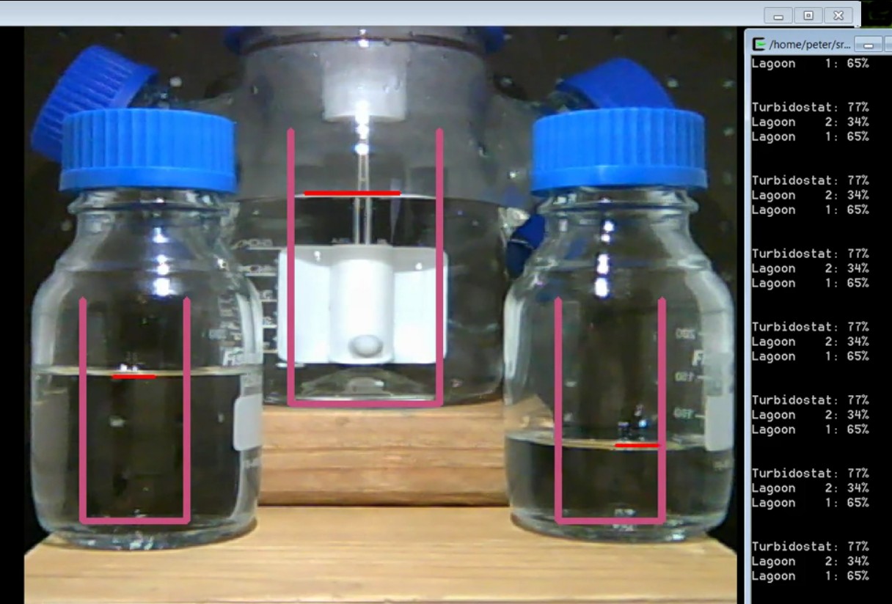
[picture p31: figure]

## Conclusions

  PACE
- Can observe evolutionary divergence and convergence in different lagoons.
- Inexpensive and fast to modify a gene
- Multiple PACE stages can radically alter genes (e.g. create a protein to recognize a new promoter)
  Implementation
- Arduino is ideal for analog inputs and real-time control a PACE device
- Low-cost system controller (Raspberry Pi) can manage multiple devices

## Material Costs for a “PACE capsule” < $1000

- Raspberry PI main computer ($40)
- Wide-angle USB or IP Camera ($100)
- Ardweeny + FTDI board ($25 X 2)
- PIR (non contact)Temperature Sensor ($50)
- Laser, LEDs, Temp IC, Photo transistor ($10)
- Insulated boxes (Uline Styrofoam) ($100)
- Heating Pads ($30)
- Magnetic Stir Motors ($20 X 5)
- Valves, Rotary valve motors ($100)
- Miscellaneous Hardware-PVC ($150)
- 5V and 12V Power Supplies ($20)
- Glassware ($200)
- Tubing + Nutrient (operating cost)

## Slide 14

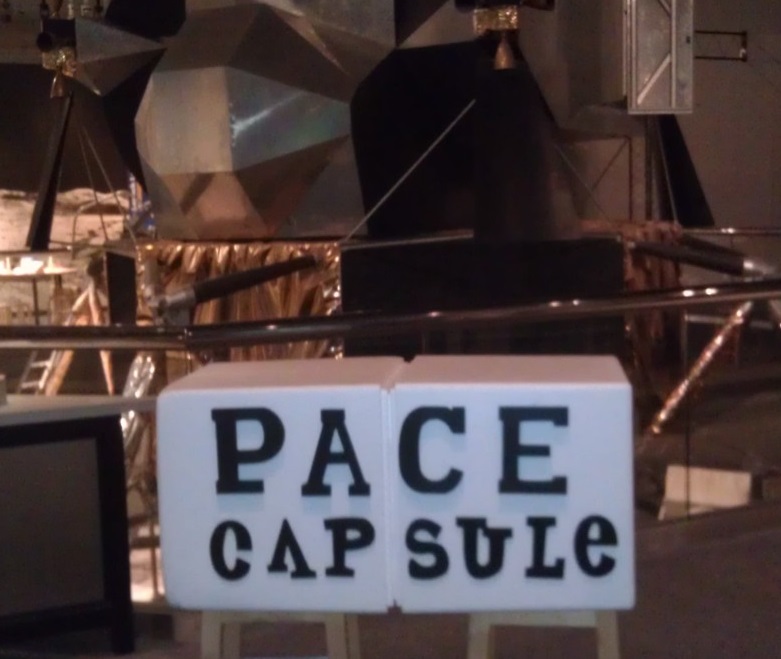
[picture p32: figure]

## More like a 'lander' after the addition of $80 worth of PCV

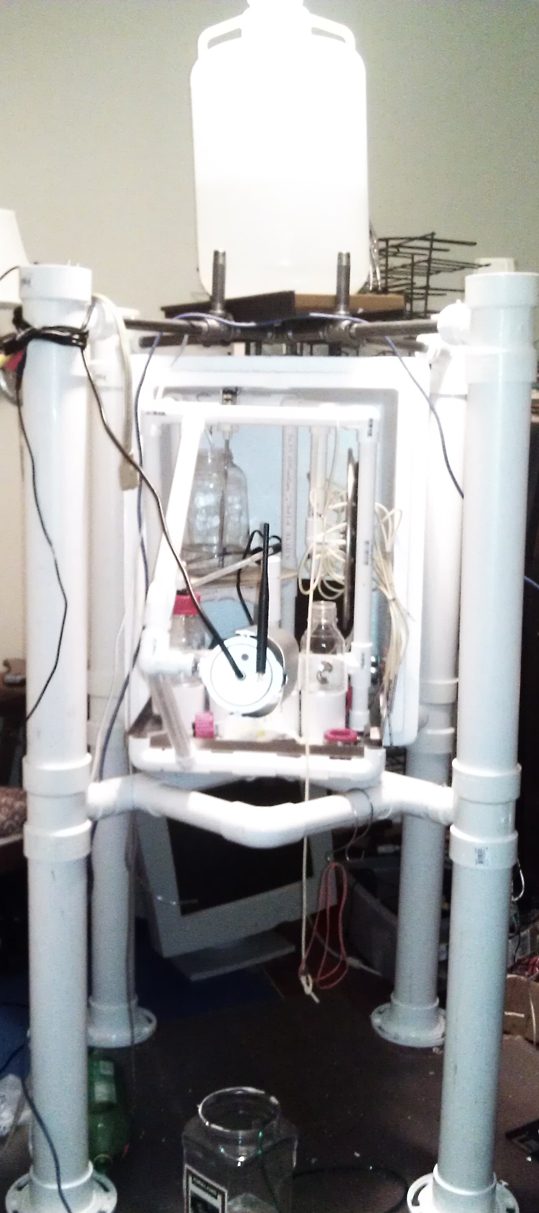
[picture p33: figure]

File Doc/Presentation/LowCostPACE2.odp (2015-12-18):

## “Evolution as a Tool”

  Phage Assisted
  Continuous Evolution
  ...on a budget

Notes: <number>

## Overview

- PACE (Esvelt et. al. Nature, April 2011 )
- Use a virus to evolve a custom protein
- Off the shelf hardware for only $30,000
  - or -
- Open-source Hardware/Software ~$1000

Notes: <number>

## Innatrix Motivation #1

- Shigella kills 1,000,000 people per year, mostly children in the developing world
- Shigella without the proteases Pic and SepA is harmless
- Hypotheses: Protease inhibiters with strong binding affinity to Pic and SepA would short-circuit Shigella's virulence
- Hypotheses: Engineered proteases produced by lactobacillus or other probiotic could provide inexpensive, long-term immunity

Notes: <number>

## Technology Potential

- Protein binding affinity is the principal characteristic of metabolic processes and pharmaceuticals
- Higher binding affinity would lower dosage for any protein therapeutic
- Large protein molecules have reduced side-effect potential over small-molecule pharmaceuticals which easily cross metabolic barriers and have more interaction potential
- Proteins degrade quickly in waste stream
- Proteins can be easily metabolized without stressing renal function

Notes: <number>

## PACE: Phage Assisted Continuous Evolution

  Evolution: Selection and Mutation
- E. coli rewards improvements to evolving protein by providing a protein that increases viral infection
- Virus replicates inside E. coli which uses an error-prone DNA polymerase to increase mutations

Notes: <number>

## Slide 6

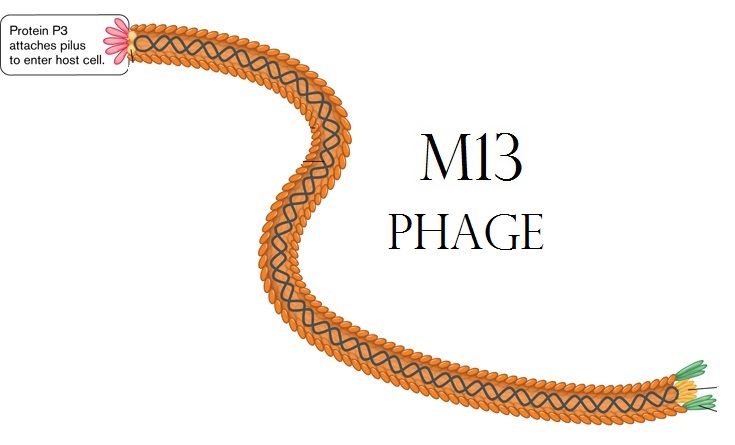
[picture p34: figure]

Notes: <number>

## PACE: Phage Assisted Continuous Evolution

- M13 virus (phage) but substitute sequence to evolve for its fusion gene
- E. coli with two extra plasmids (chromosomes)
  - Mutation: Arabinose activated mutagenesis
    (error-prone DNA polymerase)
  - Selection: M13 'fusion' gene activated by
    a particular protein interaction
  - E. coli host cells flow through “lagoons”
  containing populations of evolving viruses

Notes: <number>

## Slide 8

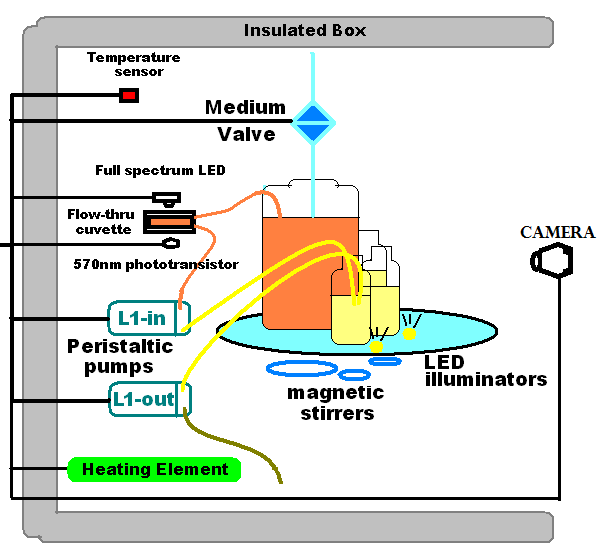
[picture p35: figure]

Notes: <number>

## Turbidostat version 1.0


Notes: <number>

## Non-contact level-sensing


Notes: <number>

## Material Costs for a “PACE capsule” < $1000

- Raspberry PI main computer ($40)
- Wide-angle USB or IP Camera ($100)
- Ardweeny + FTDI board ($25 X 2)
- PIR (non contact)Temperature Sensor ($50)
- Laser, LEDs, Temp IC, Photo transistor ($10)
- Insulated boxes (Uline Styrofoam) ($100)
- Heating Pads ($30)
- Magnetic Stir Motors ($20 X 5)
- Valves, Rotary valve motors ($100)
- Miscellaneous Hardware-PVC ($150)
- 5V and 12V Power Supplies ($20)
- Glassware ($200)
- Tubing + Nutrient (operating cost)

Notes: <number>

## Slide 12


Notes: <number>

## More like a 'lander' after the addition of $80 worth of PCV


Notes: <number>

## Know Wonder Moment


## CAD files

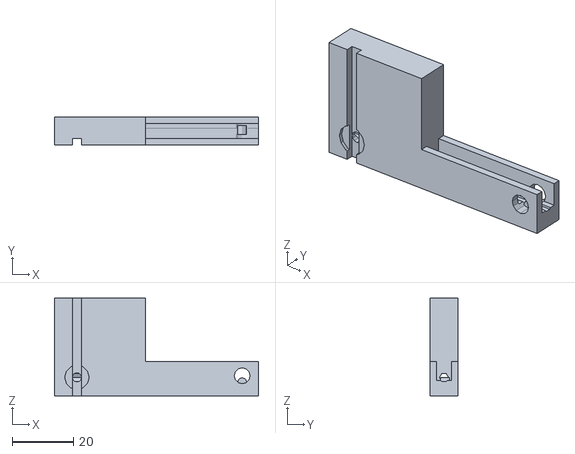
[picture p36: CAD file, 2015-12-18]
Cad/compress.stl
66.7 x 9.00 x 32.0

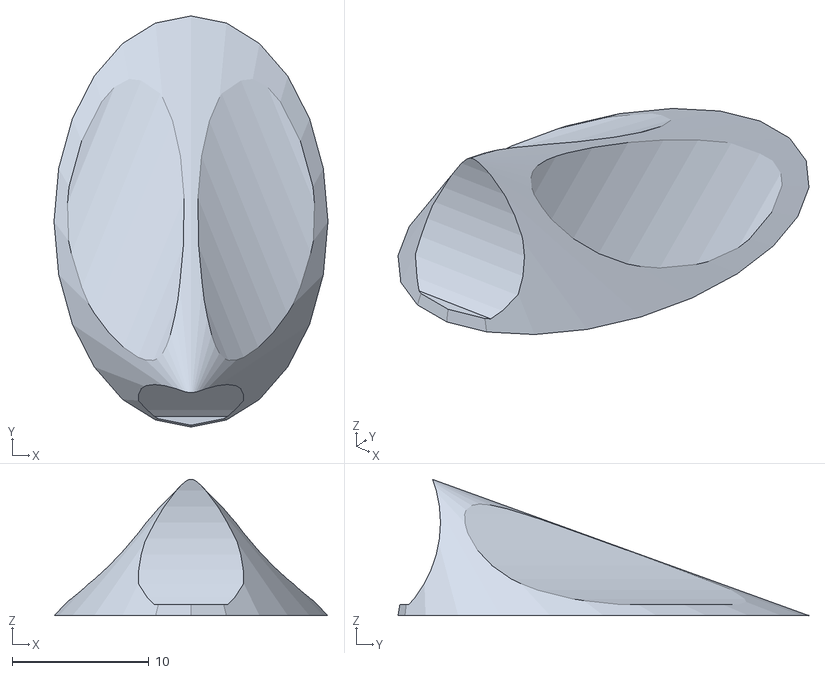
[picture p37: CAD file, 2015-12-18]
Cad/scale.stl
20.0 x 30.0 x 9.95

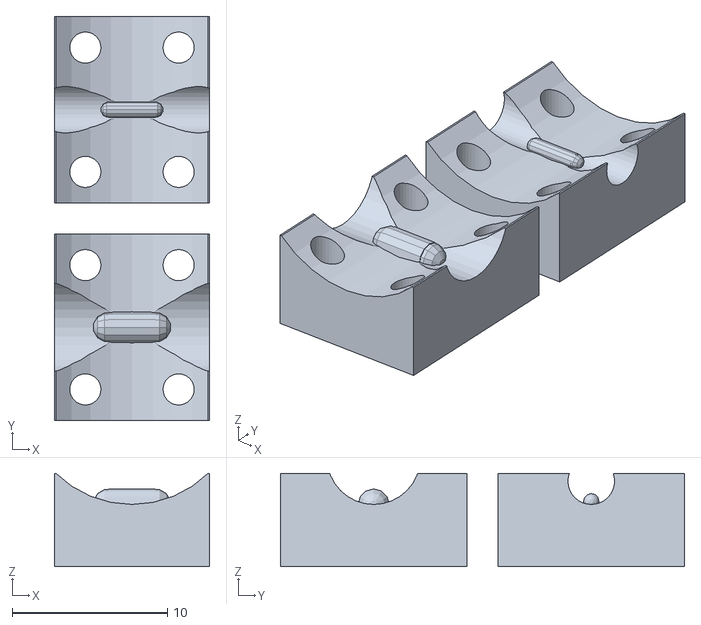
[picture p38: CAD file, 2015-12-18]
Cad/spair.stl
10.0 x 26.0 x 6.00

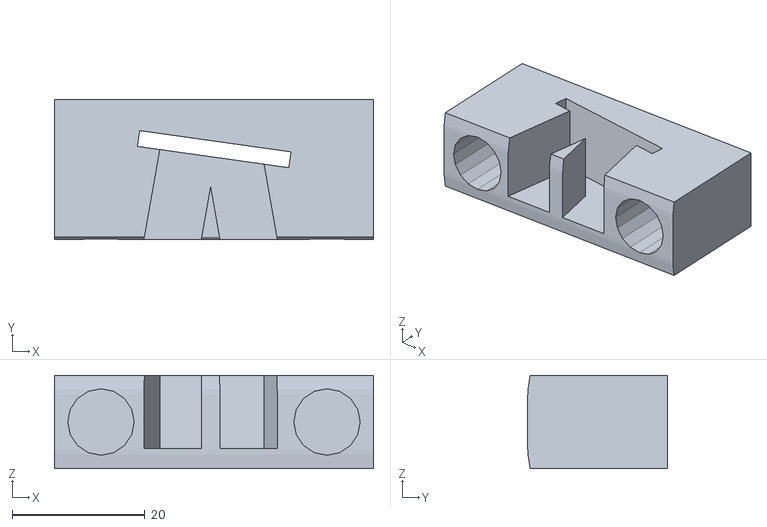
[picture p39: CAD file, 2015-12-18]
Cad/mirrorobscura.stl
48.0 x 21.0 x 14.0

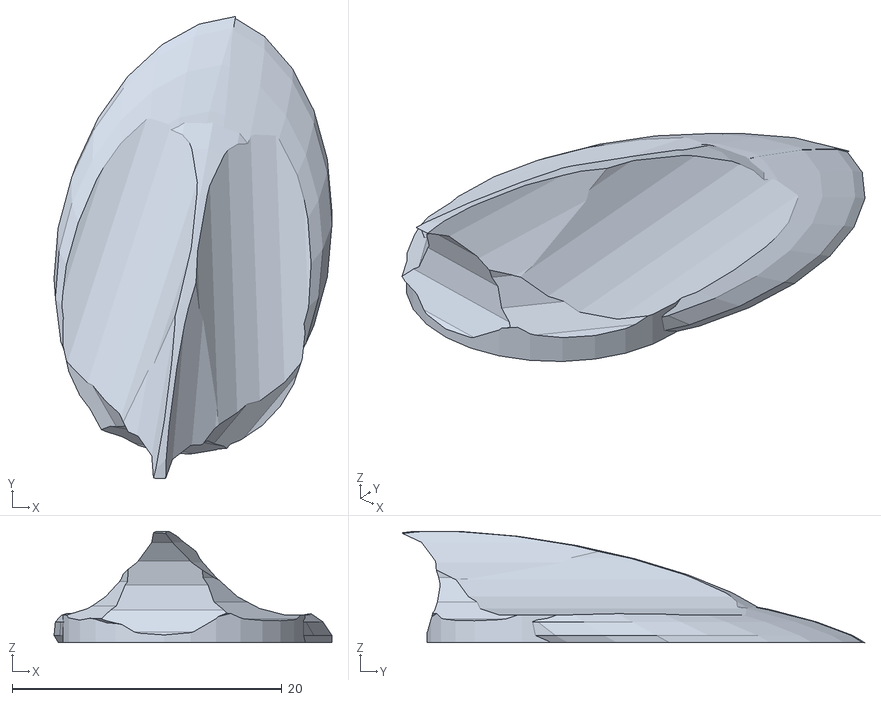
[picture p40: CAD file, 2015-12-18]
Cad/realistic2.stl
20.6 x 34.3 x 8.25

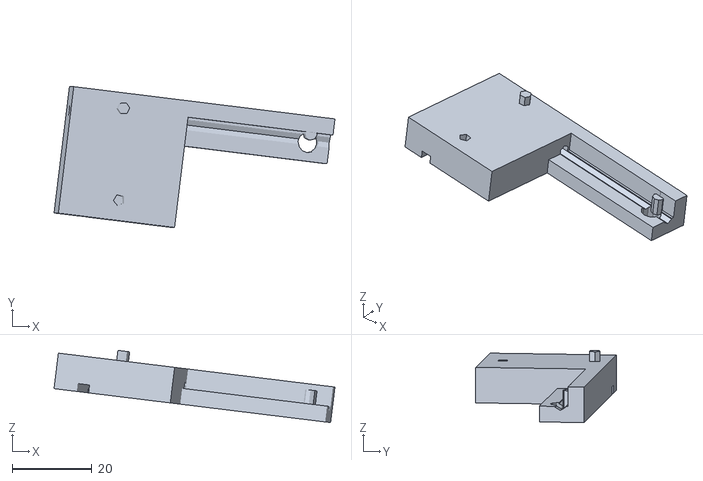
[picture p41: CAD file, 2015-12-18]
Cad/compress3.stl
70.6 x 35.4 x 18.2

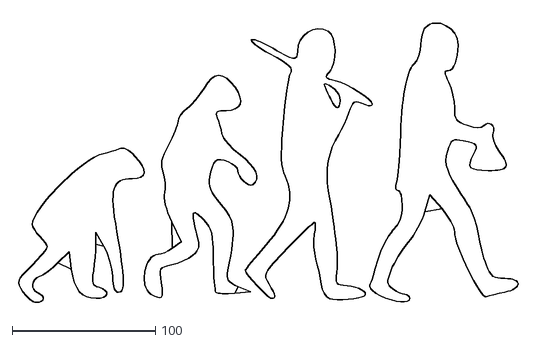
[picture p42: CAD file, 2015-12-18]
Cad/sprogress.dxf
354.0 x 201.3

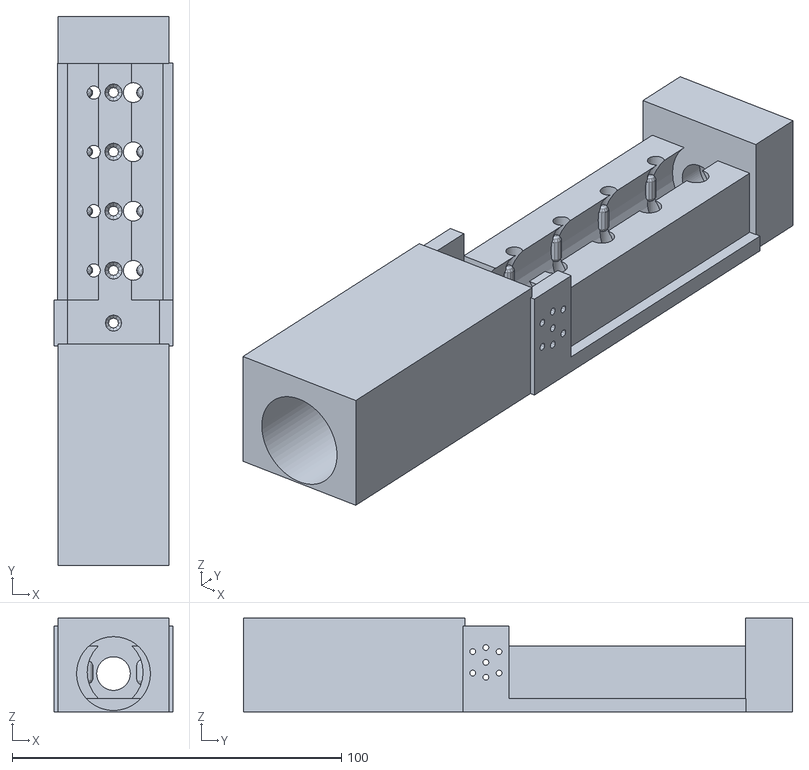
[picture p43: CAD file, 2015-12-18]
Cad/samplemotor.stl
36.0 x 166.7 x 28.4

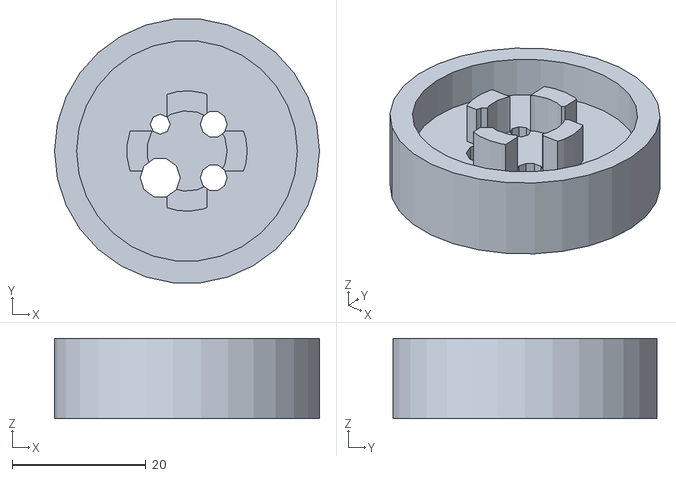
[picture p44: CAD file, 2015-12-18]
Cad/lagoon100cap.stl
39.6 x 39.4 x 12.0

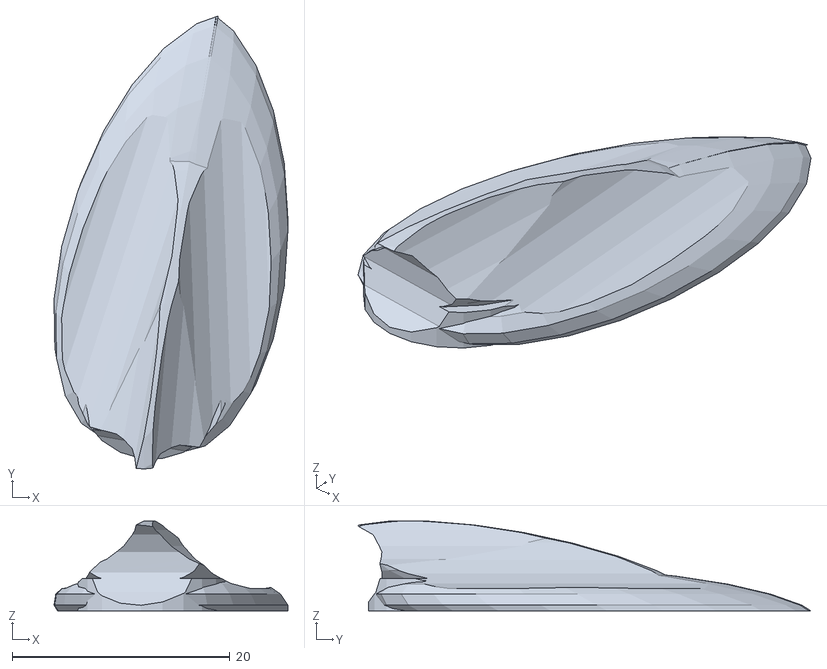
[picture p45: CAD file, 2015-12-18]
Cad/realistic.stl
21.5 x 41.6 x 8.25

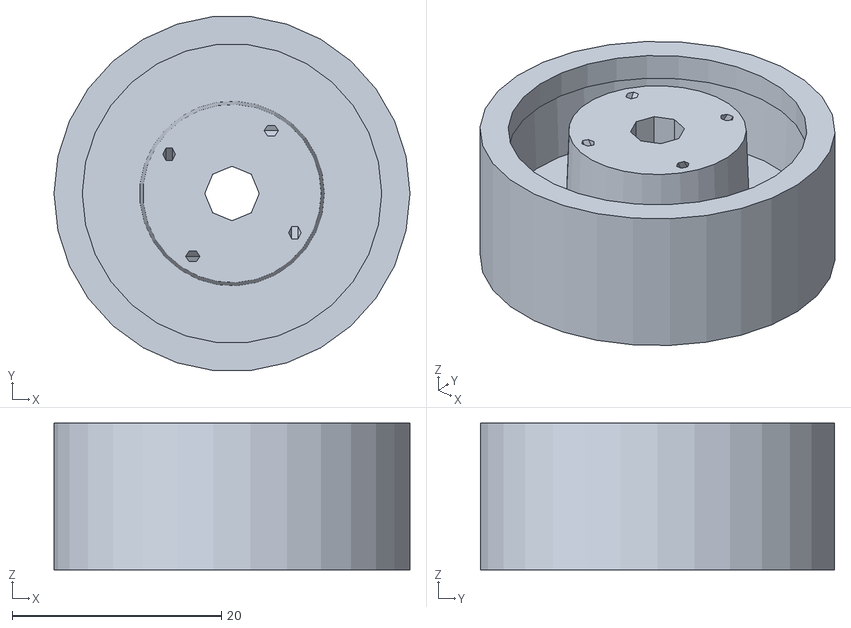
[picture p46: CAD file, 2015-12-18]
Cad/stopper.stl
34.0 x 33.8 x 14.0

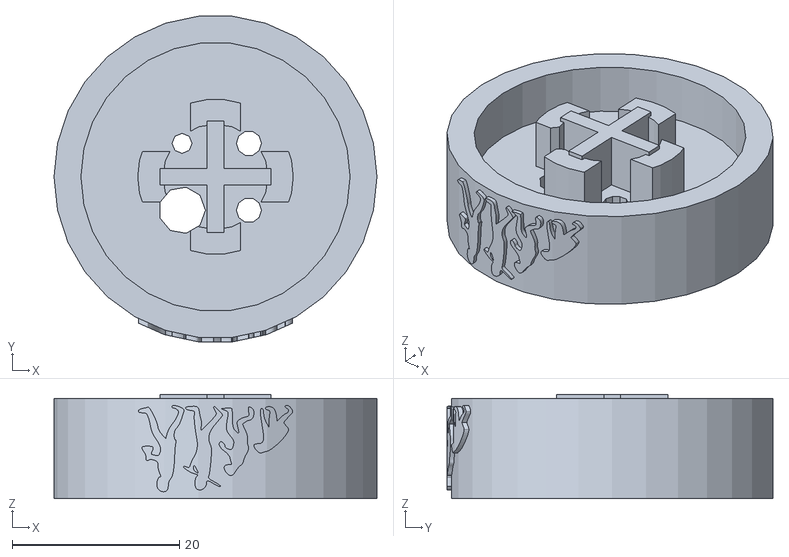
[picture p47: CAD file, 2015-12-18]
Cad/logosmallcap.stl
38.6 x 39.0 x 12.5

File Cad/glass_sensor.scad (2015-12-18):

//
// Optical sensor to receive glass tube.
//
// dimensions subject to change, see variables
// at the bottom of this file
// 

module sensor()
{

  // Optical hole


	difference() {
	// BODY (to be subtracted from)
   cube([length,width,thick],center=true);

	// Glass Tube Conduit
	   rotate([0,90,0])
        cylinder(r=dia/2, h=lengthplus, center=true, $fn=smooth);
  // Slot
     translate([0,0.5+3*dia/2,0])
        cube([lengthplus,3*dia,dia+1],center=true);

  // Optical hole
     cylinder(r=lighthole, h=thickplus/2, center=true, $fn=smooth);

  // LED Holder
    translate([0,0,thick/2])
     cylinder(r=heatsinkradius, h=4, center=true, $fn=smooth);

    translate([0,0,thick/3])
     cylinder(r=ledradius, h=thick/4, center=true, $fn=smooth);

  // Phototransistor holder
    translate([0,0,2-thick/3])
     cylinder(r=phototransradius, h=1+thick/4, center=true, $fn=smooth);

// Phototansistor leads
     translate([1,0,-thick/2]) 
       cylinder(r=0.5, h=thickplus/2, center=false, $fn=smooth);
     translate([-1,0,-thick/2]) 
       cylinder(r=0.5, h=thickplus/2, center=false, $fn=smooth);

  } // end difference

  smooth = 8;  // Number of facets for round features
	length = 80; // mm   (76mm = 3") Main Block
	width  = 30; // mm
	thick = 20;  // mm
   dia  = 6.4;  // 1/4 inch in mm
  heatsinkradius = 25.4*(7/16);
  ledradius = 3;
  phototransradius = 2.1;
	thickplus = thick + 2;  // plus margin
  lengthplus = length + 2;

}

rotate([90,0,0]) sensor();

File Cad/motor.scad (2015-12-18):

module mount(inner, length) {
side = (inner+6)/3;

	difference() {
     union() {
		cylinder(r=inner+4, h=length, center=true);
	    translate([0,0,-length/3])
		cylinder(r=inner+8, h=length/4, center=true);
      }
		cylinder(r=inner, h=length+2, center=true);

	    translate([inner,-3,6.2])  // X
			cube([side,2*side,length-2], center=true);

	    translate([-inner,-3,6.2])  // -X
			cube([side,2*side,length-2], center=true);

	    translate([0,inner,6.2])     // Y
			cube([side,2*side,length-2], center=true);

	    translate([0,-inner,6.2])  // -Y
			cube([side,2*side,length-2], center=true);

    }
}

module hole(x,y,radius) {
	translate([x,y,0])
	cylinder(r=radius,h=48,center=true);
}

module base(outer, inner, height) {
	difference() {
	  cylinder(r=outer, h=height, center=true);
	  cylinder(r=inner, h=height+2, center=true);
    }
}



// motor_radius = 18.5;
motor_radius = 18.5;
long = 25;
shaft = 6.5;
motor_offset = 7;
offset = 18.5;

difference() {
 union() {
  base(1.8*motor_radius, shaft, 6);
  translate([0,motor_offset,long/2])
	  mount(motor_radius, long);

  }
  translate([0,motor_offset,0])
	  cylinder(r=13.4,h=10,center=true);
	hole(offset,0,2.7);
	//  hole(0, offset, 1);
	hole(-offset,0,2.7);
	hole(0,-offset,2.7);
 }

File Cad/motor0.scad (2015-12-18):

module mount(outer, length) {
	difference() {
     union() {
		cylinder(r=outer, h=length, center=true);
	    translate([0,0,-length/3])
		cylinder(r=outer+6, h=length/4, center=true);
      }
		cylinder(r=outer-3, h=length+2, center=true);
	    translate([outer-3,0,0])  // X
			cube([outer/3,outer/3,length+2], center=true);

	    translate([-(outer-3),0,0])  // -X
			cube([outer/3,outer/3,length+2], center=true);

	    translate([0,outer-3,0])     // Y
			cube([outer/3,outer/3,length+2], center=true);

	    translate([0,-(outer-3),0])  // -Y
			cube([outer/3,outer/3,length+2], center=true);

    }
}

module hole(x,y,radius) {
	translate([x,y,0])
	cylinder(r=radius,h=24,center=true);
}

module base(outer, inner, height) {
	difference() {
	  cylinder(r=outer, h=height, center=true);
	  cylinder(r=inner, h=height, center=true);
    }
}



motor_radius = 18.5;
long = 25;
shaft = 6;
motor_offset = 7;
offset = 18.5;

difference() {
 union() {
  base(1.7*motor_radius, shaft, 5);
  translate([0,motor_offset,long/2])
	  mount(motor_radius, long);
  }
	hole(offset,0,1.7);
	//  hole(0, offset, 1);
	hole(-offset,0,1.7);
	hole(0,-offset,1.7);
 }

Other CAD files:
Cad/samplemotor.scad
Cad/Eppie.scad
Cad/Pulley10mm10t.scad
Cad/Pulley6mm9t.scad
Cad/auto.scad
Cad/auto1.scad
Cad/auto2.scad
Cad/baffle11.scad
Cad/black4bevel.scad
Cad/cellstat.scad
Cad/cellstatalpha.scad
Cad/cellstatbeta.scad
Cad/cellstatcap.scad
Cad/cellstatcaplogo.scad
Cad/cellstatdelta.scad
Cad/cellstatepsilon.scad
Cad/cellstateta.scad
Cad/cellstatgamma.scad
Cad/cellstatheta.scad
Cad/cellstatiota.scad
Cad/cellstatkappa.scad
Cad/cellstatlambda.scad
Cad/cellstatmu.scad
Cad/cellstatzeta.scad
Cad/clip.scad
Cad/clip0.scad
Cad/clip2.scad
Cad/collar.scad
Cad/compress.scad
Cad/compress3.scad
Cad/compressNov.scad
Cad/compressSmoothslot.scad
Cad/core4.scad
Cad/cryocam.scad
Cad/customizable_hose_tee.scad
Cad/cuvettebulge.scad
Cad/cuvettebulge2.scad
Cad/cuvetteholder.scad
Cad/dremelfuge.scad
Cad/ecoliseum.scad
Cad/ecoliseumarray.scad
Cad/fatdremelfuge.scad
Cad/flatmirror.scad
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

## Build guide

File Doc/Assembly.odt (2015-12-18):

The EvoStat

Evolution: on your schedule

This document describes the construction of an automated phagestat to maintain an evolving population of bacterial virus. The current device was designed to maintain a population of M13 phage using a supply of E. coli host cells but could be used for directed evolution of other organisms as it manages temperature, turbidity, reagent concentrations, and precise flow control.

Software for EvoStat

MAIN PROGRAM: INITIALIZE, RUN

INITIALIZE:

Arduino discovery and initialization

Light testing (verify closed chamber)

Level detection, Prime Sequence if necessary

RUN

for(i=0;i<normalcycles;i++)

if (temperature[t] < set_temp[t])

heater(t,ON);

else heater(t,OFF);

if (!check level) re-calibrate flow rate

if (turbidity > setpoint) open nutrient valve

if (bioluminescence) report activity

check temperature:

check nutrient temperature

check host cell temperature

check lagoon temperatures

Arduino Command Reference

d – dump parameter values

s – save current values in EEPROM

r – restore parameter values from EEPROM

l1 – level detection (meniscus) lights on

l0 – level detection (meniscus) lights off

d

pN1 – pump N on

pN0 – pump N off

vN1 – valve N on

vN0 – valve N off

hN1 – heater N on (auto temperature control)

hN0 – heater N off (no temperature control)

Heaters 1-4=Lagoons, 5=Host Cells, 6=Nutrient Preheater

Pumps 1=Nutrient,2=Host Output,3=Inducer1,4=Inducer2,5=Waste

Valves 1=Nutrient,2=Host Output,3=Inducer1,4=Inducer2,5=Waste

Arduino Acquisition and Initialization

Logging

Calibrate Flow-Rate

V30,V40,V50 -Host Cells into lagoons, no lagoon outflow

monitor level increase rate and adjust timings 1-4

V30,V40,V20,V51 – Lagoon outflow only

monitor level decrease and adjust timings 13-16

V31, V40, V20,V50 – Inducer1 inflow only

monitor level increase and adjust timings 5-8

V30,V41,V20,V50 – Inducer 2 inflow only

monitor level increase and adjust timings 9-12

EvoStat part list with ordering information

Qnty | Description | URL | Price
10 | 3A rectifier diodes | Jameco diode (http://www.jameco.com/webapp/wcs/stores/servlet/ProductDisplay?langId=-1&storeId=10001&catalogId=10001&productId=36249) | 100 @ $10.00
2 | 71 RPM 12VDC gearhead motor | Jameco #155855 (http://www.jameco.com/webapp/wcs/stores/servlet/Product_10001_10001_155855_-1) | 1 @ $21.95
16 | Compression Valve Fitting (ABS) | 3D Printer | -
1 | Compression Valve Pointer (ABS) | 3D Printer | -
16 | ³/32 Stainless Steel Welding Rod 4” | | -
1 | Chicago Metal 14” pizza crisper pan
5 | 12V DC Peristaltic pump
5 | 12V DC N/C valve
32 | 1K 1% metal film resistors | DigiKey resistors (http://www.digikey.com/product-detail/en/RNMF14FTC1K00/S1KCATR-ND/2617302) | 5000 @ 42.75
2 | 10ft ¾” PVC pipe | Lowes / Home Depot
1 | 10ft 3” PVC pipe | “
4 | ¾ X ¾ X 1 PVC elbow | “
4 | Sample valve fitting | 3D Printer
4 | ¼-20 anodized speed nut
1 | 12” 4.75mm (.1875”) stainless steel rod | Online Metals (https://www.onlinemetals.com/merchant.cfm?pid=4474&step=4&showunits=mm&id=7&top_cat=1) | 0.80
1 | Surplus image scanner + stepper motor | Triangle E-cycling? | -
| RJ-45 inline couplers | Amazon (http://www.amazon.com/Coupler-White-Ethernet-cables-Digital-SECURE®/dp/B00GE1DHNQ) | 12 @ 12.00
| Ethernet cables w/ RJ-45 plugs
1 | Ardweeny (auto sampler controller) | Solarbotics (https://solarbotics.com/product/kardw/) | 9.95
1 | Arduino Mega 2650 (main controller) | Amazon Mega 2650 (http://smile.amazon.com/Ximico-Arduino-Cable-Atmega2560-16au-Compatible/dp/B00KG3SBE8) | 14.99
| FOR WIRELESS LAGOONS:
4 | Arduino Mini Pro (5V 16Mhz 368) | MinInTheBox (http://www.miniinthebox.com/arduino-pro-mini-module-atmega328-5v-16m_p685134.html?litb_from=sysmail) | $3.95
4 | Bluefruit EZ-link (Bluetooth FTDI) | AdaFruit (http://www.adafruit.com/products/1588) | $22.50
4 | HC-06 (alternative Bluetooth/slave only) | MiniInTheBox (http://www.miniinthebox.com/hc-06-wireless-bluetooth-transceiver-rf-main-module-serial-for-arduino_p903460.html?litb_from=sysmail) | $4.79
4 | ULN2003 | JameCo (http://www.jameco.com/webapp/wcs/stores/servlet/Product_10001_10001_34278_-1) | 0.35
1 | 7X9cm pre-drilled PC board 276-168 | Radio Shack (http://www.radioshack.com/universal-component-pc-board-with-780-holes/2760168.html#start=1) | $3.49
1 | Connectors | MiniInTheBox (http://www.miniinthebox.com/dupont-wire-female-to-female-cable-line-41p-41p-test-lines-connector-10cm-201211270080013_p480341.html?litb_from=sysmail) | $1.99
1 | Melexis 90614 PIR Temp sensor | DigiKey (http://www.digikey.com/catalog/en/partgroup/mlx90614-15/20353) | $27.22
1 | Heating wrap for Nutrient | Carboy Heater (http://www.amazon.com/Fermentap-FE650-FermWrap-Heater/dp/B0064O92WS)
1 | Foscam 1.3M Wireless Outdoor Camera alt/ Microsoft LifeCam VX-5000 | Foscam (http://foscam.us/foscam-fi9805p-wireless-ip-camera.html) | $259.99
8 | Multi-color RJ-45 jacks | Amazon (http://www.amazon.com/Cmple-Cat6-RJ45-Punch-Keystone/dp/B0050P2TPO?s=electronics) | 4.99 each
8 | Multi-color cables | Cable Matters (http://www.amazon.com/Cable-Matters-8-Color-Snagless-Ethernet/dp/B00HSSUZO8/ref=pd_cp_pc_2) | 11.99
2 | 1 ¼” stainless steel hose clamp
100 | ½” #6 flat phillips sheet metal screws

Assemblies

1. Rotary Valve Assembly (1)
2. Priming pumps with valves (4)
3. Host Cell Stand – magnetic mixer + LED light + heater (1)
4. Lagoon Stands - magnetic mixer + LED light + heater (4)
5. Optical assembly (LED's, laser, PIR temperature sensor) (1)
6. Camera Mount
7. Stainless steel containment pan with leak sensors
8. Four-channel Auto sampler
9. Arduino Mega 2650 system controller

Connections

Four RJ-45 sockets on the main controller board connect to the four sub-systems.

Temp includes the main Host Cell container heating element (1 output) and the PIR temperature sensor (+5V, SCL, SDA, Gnd) and position feedback for Rotary Valve (Rotary In)

Flow connects to the first three priming pumps and valves (6 outputs Host, Inducer, Waste) and Rotary Valve motor (1 output plus 12VDC)

Mixers connects to the magnetic mixers for the host cell container and four lagoons (5 outputs), the host cell nutrient valve (1 output) and aeration (1 output), plus 12VDC mixer supply.

Lights connects to seven outputs: yellow meniscus lighting, white camera light, white, blue, green, and red backlight LEDs, laser, and 12VDC source.

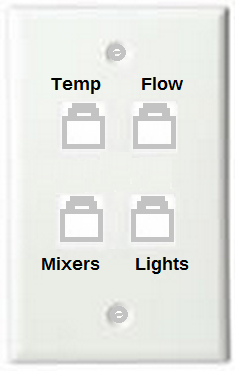
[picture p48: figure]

Ethernet cable connections: Lights
Orange | + 12V
Orange-white | Yellow LED
Green | Green LED
Green-white | White LED
Blue | Blue LED
Blue-white
Brown | Laser
Brown-white | Red

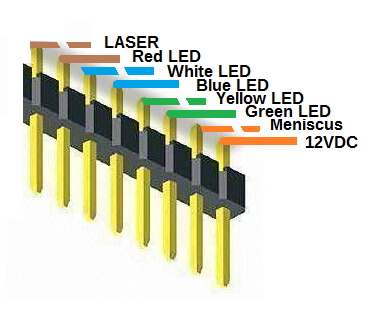
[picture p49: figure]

Ethernet cable connections: Mixers
Orange | + 12V
Orange-white
Green | Host Cell container
Green-white
Blue | Lagoon 1
Blue-white | Lagoon 2
Brown | Lagoon 3
Brown-white | Lagoon 4

Ethernet cable connections: Flow (Pumps and Valves)
Orange | + 12V
Orange-white | Rotary Valve Motor
Host Cell supply
Green | Pump 1
Green-white | Valve 1
Mutagenesis Inducer supply
Blue | Pump 2
Blue-white | Valve 2
Lagoon Outflow (waste)
Brown | Pump 3
Brown-white | Valve 3

Ethernet cable connections: Temperature Sensor/Heat control
Orange | + 5V
Orange-white | SCL
Green | Ground
Green-white | SDA
Blue | Lagoon Heaters
Blue-white | Chamber Heat
Brown | Nutrient Heat
Brown-white | Host Cell heat

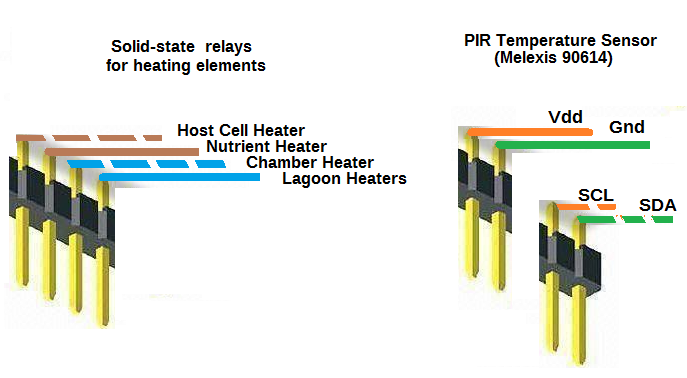
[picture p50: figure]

Length | type | diameter
1” | ring | 2”
1” | split | 2”
1” | split | 1.5”
1” | 2 spacers | 1.5”
1.5” | Double split | 3/4”

System Diagram

Cellstat

System Controller

Raspberry Pi

Phagestat

Lagoon Controller

Arduino

Phagestat

Lagoon Controller

Arduino

Phagestat

Lagoon Controller

Arduino

Phagestat

Lagoon Controller

Arduino

Bluetooth

RF Link

Raspberry Pi

Debian Linux

Remote Desktop

OpenCV

Python

Bluetooth Serial

Nutrient

pump + valve

Host Cell

pump + valve

Waste/Samplepump + valve

camera

magnetic mixer

aeration

Cellstat

Nutrient heater Host cell heater

PIR Temp Sensor

lights

Bluetooth

Communication

Bluetooth Serial

Arduino

Mini Pro

mixer

light

heater

T sensor

valve

valve

valve

valve

Phagestat

1 of 4

Software Architecture

Raspberry Pi:

1. Level detection (levelapp.py, observe.py)
2. Turbidity measurement (turbid.py)
3. Bioluminescence detection (fluor.py)
4. Temperature controls (Nutrient, Inducers, Host culture)
5. Light control
6. Logging
7. Sampling? (currently stand-alone auto-sampler)

Arduino:

1. lagoon.ino (main controller routine)
  Controls magnetic mixer and meniscus light via commands from the system controller, regulates lagoon temperature using local temperature sensor
2. valves.h (multiple valve controller object)
  Autonomously opens valves on a regular schedule which is then adjusted via communication with the System controller, which has eyes on the liquid levels
3. pid.h (PID controller object)
  Proportional/Integral/Differential temperature/heater control

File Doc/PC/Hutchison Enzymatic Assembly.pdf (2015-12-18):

# Enzymatic assembly of DNA molecules up to several hundred kilobases

Daniel G Gibson¹, Lei Young¹, Ray-Yuan Chuang¹, J Craig Venter¹,2, Clyde A Hutchison III² &
Hamilton O Smith²

We describe an isothermal, single-reaction method for assembling multiple overlapping DNA molecules by the concerted action of a 5¢ exonuclease, a DNA polymerase
and a DNA ligase. First we recessed DNA fragments, yielding single-stranded DNA overhangs that specifically annealed, and then covalently joined them. This assembly method can be used to seamlessly construct synthetic and natural genes, genetic pathways and entire genomes, and could be a useful molecular engineering tool.

For nearly 40 years, scientists have had the ability to join DNA sequences and produce combinations that are not present in nature. This ‘recombinant DNA technology’ was initiated soon after the discovery of DNA ligase¹ and restriction endonucleases². Since then, multiple approaches for joining DNA molecules through the use of restriction enzymes³,4 and PCR⁵⁻⁸ have been adapted. Ligation-independent cloning strategies have also been developed⁹,10. We had recently described an in vitro recombination method that we had used to join 101 DNA cassettes into four quarter molecules of the Mycoplasma genitalium genome, each 136–166 kilobases (kb)¹¹ (Supplementary Figs. 1–3 and Supplementary Results online). Because we performed this recombination method in a thermocycler (to which we refer as ‘thermocycled’ here), individual reactions were carried out in only two steps. Here we improved this two-step thermocycled method by using exonuclease III and antibody-bound Taq DNA polymerase, which allow for one-step thermocycled in vitro recombination (Supplementary Fig. 4 and Supplementary Results online).
We now present an in vitro recombination system that differs from the ones above by its capacity to assemble and repair overlapping DNA molecules in a single isothermal step. This approach can be used to join DNA molecules that are as large as 583 kb and to clone joined products in Escherichia coli that are as large as 300 kb. All reagents and enzymes are commercially available, and all that is required for DNA assembly is for the reagent-enzyme mix (which can be stored at 20 1C until needed) to be combined with overlapping DNA molecules and then incubated at 50 ¹C for as few as 15 min (Online Methods). This approach dramatically simplifies the construction of large DNA molecules from constituent parts. Exonucleases that recess double-stranded DNA from 5¢ ends will not compete with polymerase activity. Thus, all enzymes required for DNA assembly can be simultaneously active in a single isothermal reaction. Furthermore, circular products can be enriched as they are not processed by any of the three enzymes in the reaction. We optimized a 50 1C isothermal assembly system using the activities of the 5¢ T5 exonuclease (Epicentre), Phusion DNA polymerase (New England Biolabs (NEB)) and Taq DNA ligase (NEB) (Fig. 1). Taq DNA polymerase (NEB) can be used in place of Phusion DNA polymerase (data not shown), but the latter is preferable as it has inherent proofreading activity for removing noncomplementary sequences (for example, partial restriction sites) from assembled molecules.
To test this system, we cleaved two restriction fragments that overlapped by B450 base pairs (bp) from the 6-kb pRS415 vector and then reassembled them into a circle (Fig. 2a). After 6–8 min at 50 1C, the linear substrate DNA was completely reacted, and the major product was the 6-kb circle, which migrated just below the 4-kb linear position on an agarose gel. T5 exonuclease actively degrades linear DNA molecules, but closed circular DNA molecules are not degraded¹². We confirmed the circularity of this assembled product by treating it with additional T5 exonuclease (Fig. 2a). To demonstrate that this assembled product was the predicted 6-kb circle, we digested it with Not I (a single-cutter) and observed the

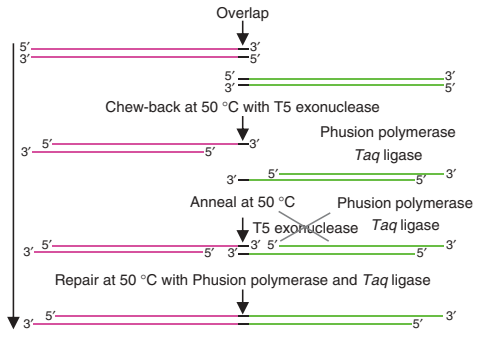
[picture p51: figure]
Chew-back at 50 °C with T5 exonuclease; Overlap; Anneal at 50 °C; Phusion polymerase; T5 exonuclease; Taq ligase

Repair at 50 °C with Phusion polymerase and Taq ligase

Figure 1 | One-step isothermal in vitro recombination. Two adjacent DNA
fragments (magenta and green) sharing terminal sequence overlaps (black) were joined into a covalently sealed molecule in a one-step isothermal reaction. T5 exonuclease removed nucleotides from the 5¢ ends of double-stranded DNA molecules, complementary single-stranded DNA overhangs annealed, Phusion DNA polymerase filled the gaps and Taq DNA ligase sealed the nicks. T5 exonuclease is heat-labile and is inactivated during the 50 1C incubation.

RECEIVED 5 JANUARY; ACCEPTED 16 MARCH; PUBLISHED ONLINE 12 APRIL 2009; DOI:10.1038/NMETH.1318 (http://www.nature.com/doifinder/10.1038/NMETH.1318)

1The J. Craig Venter Institute, Synthetic Biology Group, Rockville, Maryland, USA, and 2San Diego, California, USA. Correspondence should be addressed to D.G.G. (dgibson@jcvi.org).

NATURE METHODS | VOL.6 NO.5 | MAY 2009 | 343

## BRIEF COMMUNICATIONS

© 2009 Nature America, Inc. All rights reserved.

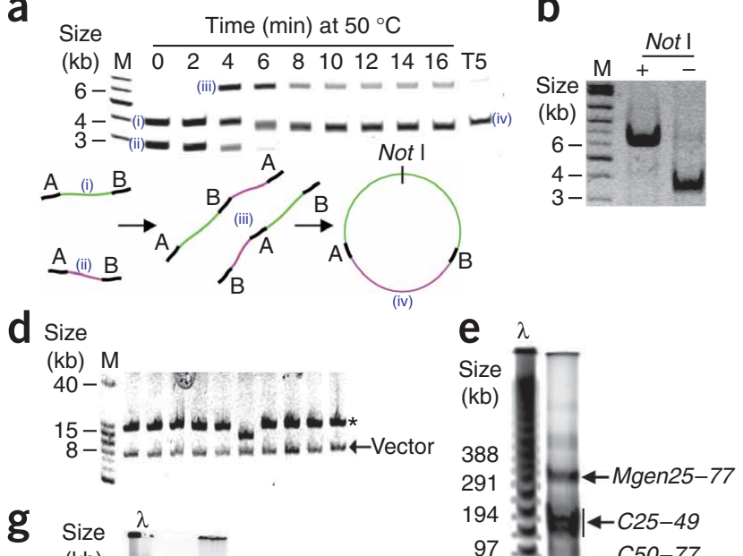
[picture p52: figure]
g Size; Time (min) at 50 °C; Size (kb); Not l; (iii); Size (kb) 40; Vector * 8; Not I; Mgen25–77

6-kb linear fragment (Fig. 2b). We concluded that DNA molecules can be assembled and repaired in a single isothermal step using this method.
We next determined whether DNA molecules with overlaps of only 40 bp could be joined. We accomplished this when we reduced the concentration of T5 exonuclease (Fig. 2c). Three 5-kb DNA fragments, F1–F3, were efficiently assembled into an 8-kb bacterial artificial chromosome (BAC). Furthermore, when we transformed these assembled DNA molecules into E. coli, we obtained 4,500 colonies, and nine out of ten colonies tested had the predicted 15-kb insert (Fig. 2d).
During the construction of the synthetic M. genitalium genome, we could not use our two-step thermocycled in vitro recombination method to clone assembled DNA molecules larger than B150 kb in
E. coli¹¹. To determine whether the isothermal assembly method could be used to join and clone DNA fragments of larger size, we reacted two synthetic M. genitalium quarter DNA molecules, C25–49 (144 kb) and C50–77 (166 kb), with BAC25–77 (8 kb), a cloning vector specific for the assembly of these two DNA molecules. The 318-kb Mgen25–77 product was efficiently produced, so we conclude that DNA fragments this size can be joined by this method (Fig. 2e). To determine whether this method could be used to clone assembled DNA fragments this size, we transformed a fraction of this assembly reaction into E. coli. We obtained several hundred clones, and 5 out of 10 colonies screened had the correct insert size (310 kb; Fig. 2f). Thus, this DNA assembly system can be used to join and clone DNA molecules up to several hundred kilobases in length in E. coli, the approximate upper limit for transformation into this bacterium¹³. In a direct comparison of all our assembly methods, we found that only the one-step in vitro recombination methods could be used to clone assembled DNA fragments this size (Supplementary Fig. 5 online).
During in vitro recombination, errors may be introduced in the assembled DNA. However, sequencing of 30 cloned DNA molecules (210 repaired junctions) after two-step thermocycled assembly revealed only 4 errors (Supplementary Table 1 online). This equates to only about 1 error per 50 DNA molecules joined. Therefore, if our hierarchical scheme to assemble the M. genitalium genome was used¹¹ without sequence verification at intermediate steps, 3–4 errors would likely be present. We expect that the number of mutations would be even lower with the isothermal assembly system because gaps are filled in by Phusion DNA polymerase, which has higher fidelity than Taq polymerase.
Our isothermal method can be used to assemble DNA molecules of unprecedented sizes, and we used it to assemble the complete synthetic 583-kb M. genitalium genome (Fig. 2g). The size limit for in vitro DNA assembly is not known, but products as large as 900 kb have been observed (Supplementary Fig. 6 online). Of the three in vitro recombination methods, we prefer the one-step-isothermal system because of its simplicity. This approach could be very useful for cloning multiple inserts into a vector without relying on the availability of restriction sites and for rapidly constructing large DNA molecules. For example, regions of DNA too large to be amplified by PCR can be divided into multiple overlapping PCR amplicons and then assembled into one piece. The one-step thermocycled method could be used to generate linear assemblies as the exonuclease is inactivated during the reaction (Supplementary Figs. 4 and 5).
Synthetic biologists are engineering genetic pathways for the production of biofuels, pharmaceuticals and industrial compounds¹⁴,15. Here we provide efficient methods for constructing these pathways, from natural or synthetic DNA.

METHODS
Methods and any associated references are available in the online version of the paper at http://www.nature.com/naturemethods/.

Note: Supplementary information is available on the Nature Methods (http://www.nature.com/naturemethods/) website.

Figure 2 | Examples of the one-step isothermal
assembly method. (a) Two DNA molecules (4,024 bp, green (i) and 2,901 bp, magenta (ii)), overlapping by B450 bp at the termini (black, overlaps labeled A and B), were reacted for
0–16 min to form a 6-kb circle, pRS415 (iv). Linear assembly products (iii) were then removed by incubation with additional tenfold excess T5 exonuclease after the 16-min incubation (T5).
(b) Not I digest of the assembled circles (pRS415) shown in a.(c) Fragments F1–F3 were assembled into an 8-kb PCR-amplified pCC1BAC (Epicentre) containing 40-bp overlaps to F1 and F3, using the indicated amounts of T5 exonuclease. The B23-kb circular assembly products are indicated by the arrow. (d) Not I digestion of BACs purified from ten E. coli clones after electroporation of the 4 U ml⁻¹ T5 exonuclease reaction shown in c. *, correct 15-kb insert. (e) Assembly of quarter
M. genitalium genomes C25-49 and C50-77 with BAC25-77 (ref. 11) to produce Mgen25-77.
(f) Not I digestion of BACs purified from ten
E. coli clones after electroporation of the assembly
reaction shown in e. The correct insert size (310 kb) is indicated by the arrow. (g) Assembly of quarter M. genitalium genomes C1–24, C25–49, C50–77 and C78–101 (ref. 11) to produce a complete M. genitalium genome. DNA products were analyzed by conventional gel electrophoresis (a,b) and by field-inversion gel electrophoresis (c–g). M, 1-kb DNA extension markers; l, lambda markers.

(kb)
631
534
437
340
243
146
48.5

Complete

Three-quarters

One-half

One-quarter

f

Size
(kb)
291

194

97

Vector

λ

a

b
c

Size
(kb)

T5 exonuclease (U ml⁻¹)

40

Input

DNA

M 100
20
4

0.8

0.16
0

20
8

5

97
C50–77

BAC25–77

344 | VOL.6 NO.5 | MAY 2009 | NATURE METHODS

© 2009 Nature America, Inc. All rights reserved.

ACKNOWLEDGMENTS
This work was supported by the Office of Science (Biological and Environmental Research) United States Department of Energy grant number DE-FG02-02ER63453, and Synthetic Genomics, Inc.

AUTHOR CONTRIBUTIONS
D.G.G., L.Y., R.-Y.C., J.C.V., C.A.H. and H.O.S. designed research; D.G.G., L.Y., R.-Y.C., C.A.H. and H.O.S. performed research; D.G.G., L.Y., R.-Y.C., J.C.V., C.A.H. and H.O.S. analyzed data; and D.G.G., C.A.H. and H.O.S. wrote the paper.

COMPETING INTERESTS STATEMENT
The authors declare competing financial interests: details accompany the full-text HTML version of the paper at http://www.nature.com/naturemethods/.

Published online at http://www.nature.com/naturemethods/
Reprints and permissions information is available online at http://npg.nature.com/reprintsandpermissions/
1. Gellert, M. Proc. Natl. Acad. Sci. USA 57, 148–155 (1967).
2. Smith, H.O. & Wilcox, K.W. J. Mol. Biol. 51, 379–391 (1970).
3. Shetty, R.P., Endy, D. & Knight, T.F. Jr. J. Biol. Eng. 2, 5 (2008).
4. Yount, B., Denison, M.R., Weiss, S.R. & Baric, R.S. J. Virol. 76, 11065–11078 (2002).
5. Horton, R.M., Cai, Z.L., Ho, S.N. & Pease, L.R. Biotechniques 8, 528–535 (1990).
6. Horton, R.M. Mol. Biotechnol. 3, 93–99 (1995).
7. Bang, D. & Church, G.M. Nat. Methods 5, 37–39 (2008).
8. Geu-Flores, F., Nour-Eldin, H.H., Nielsen, M.T. & Halkier, B.A. Nucleic Acids Res. 35, e55 (2007).
9. Aslanidis, C. & de Jong, P.J. Nucleic Acids Res. 18, 6069–6074 (1990).
10. Li, M.Z. & Elledge, S.J. Nat. Methods 4, 251–256 (2007).
11. Gibson, D.G. et al. Science 319, 1215–1220 (2008).
12. Sayers, J.R. & Eckstein, F. J. Biol. Chem. 265, 18311–18317 (1990).
13. Sheng, Y., Mancino, V. & Birren, B. Nucleic Acids Res. 23, 1990–1996 (1995).
14. Endy, D. Nature 438, 449–453 (2005).
15. Drubin, D.A., Way, J.C. & Silver, P.A. Genes Dev. 21, 242–254 (2007).
NATURE METHODS | VOL.6 NO.5 | MAY 2009 | 345

© 2009 Nature America, Inc. All rights reserved.

ONLINE METHODS
Preparation of DNA molecules for in vitro recombination. The DNA molecules used in the assembly analyses were derived from several sources including (i) the assembly intermediates of the synthetic M. genitalium genome¹¹, (ii) PCR products derived from plasmids (F6 and F8), Clostridium cellulolyticum genomic DNA (F1–F4) and Mycoplasma gallisepticum genomic DNA (F5 and F7) and (iii) pRS415 restriction fragments. E. coli strains carrying each of M. genitalium cassettes 66–69 (contained in pENTR223), each of M. genitalium cassettes 78–85 (contained in pBR322), C1–24, C25–49, C50–77 and C78–101 (each contained in pCC1BAC) or pRS415 were propagated in LB medium containing the appropriate antibiotic and incubated at 30 1C or 37 1C for 16 h. The cultures were collected and the DNA molecules were purified using Qiagen’s HiSpeed Plasmid Maxi Kit according to the manufacturer’s instructions, with the exception of C1–24, C25– 49, C50–77 and C78–101, which were not column-purified. Instead, after neutralization of the lysed cells, these DNA molecules were centrifuged then precipitated with isopropanol. DNA pellets were dissolved in Tris-EDTA (TE) buffer (pH 8.0) then RNase treated, phenol-chloroform extracted and ethanol precipitated. DNA pellets were dissolved in TE buffer. Cassettes 66–69 and 78–85 were excised from the vectors by restriction digestion with either Fau I or Bsm BI and C1–24, C25–49, C50–77 and C78– 101 were excised by digestion with Not I. To generate the 4,024-bp and 2,901-bp overlapping fragments of pRS415, DNA was digested with Pvu II and Sca I or Psi I, respectively. Restriction digestions were terminated by phenol-chloroform extraction and ethanol precipitation. DNA was dissolved in TE buffer, then quantified by gel electrophoresis with known DNA standards. Fragments F1–F8 were generated by PCR using the Phusion Hot Start High-Fidelity DNA polymerase with HF buffer (NEB) according to the manufacturer’s instructions. PCR products were extracted from agarose gels after electrophoresis and purified using the QIAquick Gel Extraction kit (Qiagen) according to the manufacturer’s instructions, except DNA was eluted from the columns with TE buffer pH
8.0. Fragments F1–F4 were amplified from Clostridium cellulolyticum genomic DNA using primers F1-For and F1-Rev, F2-For and F2-Rev, F3-For and F3-Rev, and F4-For and F4-Rev, respectively. F5 and F7 were amplified from Mycoplasma gallisepticum genomic DNA using primers F5-For and F5-Rev, and F7-For and F7-Rev, respectively. F6 and F8 were amplified from pRST2 (ref. 16) using primers F6-For and F6-Rev, and F8-For and F8-Rev, respectively. Primer sequences are listed in Supplementary Table 2 online.

Two-step thermocycled DNA assembly. A4-chew-back and
anneal (CBA) reaction buffer (20% PEG-8000, 800 mM Tris-HCl pH 7.5, 40 mM MgCl2, 4 mM DTT) was used for thermocycled DNA assembly. DNA molecules were assembled in 20-ml reactions consisting of 5 ml4-

CBA buffer, 0.2 ml of 10 mg ml⁻¹ BSA (NEB) and 0.4 ml of 3 U ml

–1 T4 polymerase (NEB). T7 polymerase can be substituted for T4 polymerase (data not shown). Approximately 10–100 ng of each B6 kb DNA segment was added in equimolar amounts. For larger DNA segments, proportional amounts of DNA were added (for example, 250 ng of each 150 kb DNA segment). Assembly reactions were prepared in 0.2 ml PCR tubes and cycled as follows: 37 1C from 0 to 18 min as indicated in the text, 75 1C for 20 min, 0.1 1Cs⁻¹ to 60 1C, held at 60 1C for 30 min, then cooled to 4 1C at a rate of 0.1 1Cs⁻¹. In general, a chew-back time of 5 min was used for overlaps less than 80 bp and 15 min for overlaps greater than 80 bp. Ten microliters of the CBA reactions were then added to 25.75 ml of Taq repair buffer (TRB), which consisted of 5.83% PEG-8000, 11.7 mM MgCl2, 15.1 mM DTT, 311 mM each of the four dNTPs and 1.55 mM NAD. Four microliters of 40 U ml

–1 Taq DNA ligase and 0.25 ml of 5 U ml

–1 Taq
polymerase were added and the reactions were incubated at 45 1C for 15 min. For the T4 polymerase fill-in assembly method, 10 ml of the CBA reaction was mixed with 0.2 ml of 10 mM dNTPs and 0.2 ml of 3 U ml

–1 T4 polymerase. This reaction was carried out at 37 1C for 30 min.

One-step thermocycled DNA assembly. A4-chew-back, anneal
and repair (CBAR) reaction buffer (20% PEG-8000, 600 mM Tris-HCl pH 7.5, 40 mM MgCl2, 40 mM DTT, 800 mM each of the four dNTPs and 4 mM NAD) was used for one-step thermocycled DNA assembly. DNA molecules (added in amounts described above for CBA reactions) were assembled in 40 ml reactions consisting of 10 ml4-CBAR buffer, 0.35 ml of 4 U ml

–1 ExoIII
(NEB), 4 ml of 40 U ml

–1 Taq DNA ligase and 0.25 ml of 5 U ml

–1
Ab-Taq polymerase (Applied Biosystems). ExoIII was diluted 1:25 from 100 U ml

–1 in its stored buffer (50% glycerol, 5 mM KPO4, 200 mM KCl, 5 mM 2-mercaptoethanol, 0.05 mM EDTA and 200 mg ml⁻¹ BSA, pH 6.5). DNA assembly reactions are prepared in 0.2 ml PCR tubes and cycled using the following conditions: 37 1C for 5 or 15 min as indicated in the text, 75 1C for 20 min, 0.1 1Cs⁻¹ to 60 1C, then held at 60 1C for 1 h. In general, a chew-back time of 5 min was used for overlaps less than 80 bp and 15 min for overlaps greater than 80 bp. ExoIII is less active on 3¢ protruding termini¹⁷, which can result from digestion with certain restriction enzymes. This can be overcome by removing the overhangs to form blunt ends with the addition of T4 polymerase and dNTPs, as described above, before assembly (data not shown).

One-step isothermal DNA assembly. A5-isothermal reaction
buffer (25% PEG-8000, 500 mM Tris-HCl pH 7.5, 50 mM MgCl2, 50 mM DTT, 1 mM each of the four dNTPs and 5 mM NAD) was used for one-step DNA assembly at 50 1C. DNA molecules (added in amounts described above for CBA reactions) were assembled in 40 ml reactions consisting of 8 ml5-isothermal buffer, 0.8 ml of 0.2 U ml

–1 or 1.0 U ml

–1 T5 exonuclease, 4 ml of 40 U ml

–1 Taq DNA
ligase and 0.5 ml of 2 U ml

–1 Phusion DNA polymerase. T5 exonuclease was diluted 1:50 or 1:10 from 10 U ml

–1 in its stored
buffer (50% glycerol, 50 mM Tris-HCl pH 7.5, 0.1 mM EDTA, 1 mM DTT, 0.1 M NaCl and 0.1% Triton X-100) depending on the overlap size. For overlaps shorter than 150 bp, 0.2 U ml

–1 T5
exonuclease is used. For overlaps larger than 150 bp, 1.0 U ml

–1 T5
exonuclease was used. All isothermal assembly components can be stored at –20 1C in a single mixture at 1.33-concentration for
more than one year. The enzymes are still active after more than ten freeze-thaw cycles. To constitute a reaction, 5 ml DNA was added to 15 ml of this mixture. Incubations were carried out at 50 1C for 15 to 60 min, with 60 min being optimal.

One-step isothermal DNA assembly protocol. Six milliliters of 5-isothermal reaction buffer were prepared by combining 3 ml of 1 M Tris-HCl pH 7.5, 150 ml of 2 M MgCl2, 60 ml of 100 mM dGTP, 60 ml of 100 mM dATP, 60 ml of 100 mM dTTP, 60 ml of 100 mM dCTP, 300 ml of 1 M DTT, 1.5 g PEG-8000 and

NATURE METHODS | DOI:10.1038/nmeth.1318

© 2009 Nature America, Inc. All rights reserved.

300 ml of 100 mM NAD. This buffer can be aliquoted and stored at –20 1C. An assembly master mixture was prepared by combining 320 ml5-isothermal reaction buffer, 0.64 ml of 10 U ml

–1 T5
exonuclease, 20 ml of 2 U ml

–1 Phusion DNA polymerase, 160 ml of 40 U ml

–1 Taq DNA ligase and water up to a final volume of 1.2 ml. Fifteen microliters of this reagent-enzyme mix were aliquoted and stored at –20 1C. This mixture can tolerate numerous freeze-thaw cycles and remains stable even after one year. The exonuclease amount is ideal for the assembly of DNA molecules with 20– 150 bp overlaps. For DNA molecules overlapping by greater than 150 bp, 3.2 ml of 10 U ml

–1 T5 exonuclease was used to prepare the assembly master mixture above. Frozen 15 ml assembly mixture aliquots were thawed and then kept on ice until ready to be used. Five microliters of the DNA to be assembled were added to the master mixture in equimolar amounts. Between 10 and 100 ng of each B6 kb DNA fragment was added. For larger DNA segments, proportional amounts of DNA were added (for example, 250 ng of each 150 kb DNA segment). Incubations were performed at 50 1C for 15 to 60 min (60 min was optimal).

Rolling-circle amplification (RCA) of assembled products. RCA was carried out as previously described¹⁸. One microliter of the repaired or unrepaired reaction was mixed with 1 ml of 100 mM NaOH and incubated at room temperature (18–22 1C) for 5 min to denature the double-stranded DNA. One microliter of this alkaline-treated mixture was then added to 19 ml of RCA components in a 0.2 ml PCR tube. The final reaction concentrations for RCA are as follows: 37 mM Tris-HCl pH 7.5, 50 mM KCl, 10 mM MgCl2, 5 mM (NH4)2SO4, 100 mg ml⁻¹ BSA, 1 mM DTT, 3.25 mM random hexamers (Fidelity System), 1 U ml⁻¹ yeast pyrophosphatase (United States Biochemical) and 250 U ml⁻¹ phi29 DNA polymerase (NEB). The reaction was incubated at 30 1C for 20 h then terminated by incubation at 65 1C for 10 min.

Cloning the DNA assembly products. To clone assembled products, reactions were carried out in the presence of PCR-amplified BACs containing 40 bp of overlapping sequence to the ends of the assembled product. Not I restriction sites were also included to allow release of the vector¹¹. To produce BAC-F1/F3, primers

BACF1 For and BACF3 Rev were used in PCR. To produce BAC66-69, primers BAC66 For and BAC69 Rev were used in PCR. To produce BAC25-77, primers BAC25 For and BAC77 Rev were used in PCR. Primer sequences are listed in Supplementary Table 2. In general, pCC1BAC was used as DNA template. However, for cloning Mgen25-77, a version of pCC1BAC, named KanBAC, was constructed that contains the kanamycin resistance gene in place of the chloramphenicol resistance gene. Samples (up to 1 ml) of the assembly reactions were transformed into 30 ml TransforMax EPI300 (Epicentre) electrocompetent E. coli cells in a 1-mm cuvette (BioRad) at 1,200 V, 25 mF and 200 O using a Gene Pulser Xcell Electroporation system (BioRad). Cells were allowed to recover at 30 1C or 37 1C for 2 h in 1 ml SOC medium then plated onto LB medium containing 12.5 mg ml⁻¹ chloramphenicol or LB medium containing 25 mg ml⁻¹ kanamycin. After incubation at 30 1C or 37 1C for 24–48 h, individual colonies were selected and grown in 3 ml LB medium with 12.5 mg ml⁻¹ chloramphenicol or 25 mg ml⁻¹ kanamycin overnight at 30 1C or 37 1C. DNA was prepared from these cells by alkaline lysis using the P1, P2 and P3 buffers (Qiagen) followed by isopropanol precipitation. DNA pellets were dissolved in TE buffer containing RNase and then digested with Not I to release the insert from the BAC.

Agarose gel analyses of assembled DNA molecules and cloned products. U-5 field-inversion gel electrophoresis analysis was performed on 0.8% E-gels (Invitrogen) and the parameters were forward 72 V, initial switch 0.1 s, final switch 0.6 s, with linear ramp and reverse 48 V, initial switch 0.1 s, final switch 0.6 s, with linear ramp. U-2 field-inversion gel electrophoresis analysis was performed on 1% agarose gels (BioRad) in 1-TAE buffer with
0.5 mg ml⁻¹ ethidium bromide without circulation, and the parameters were forward 90 V, initial switch 5.0 s, final switch 30 s, with linear ramp, and reverse 60 V, initial switch 5.0 s, final switch 30 s, with linear ramp. DNA bands were visualized with a BioRad Gel Doc or an Amersham Typhoon 9410 Fluorescence Imager.
16. Lartigue, C., Duret, S., Garnier, M. & Renaudin, J. Plasmid 48, 149–159 (2002).
17. Henikoff, S. Gene 28, 351–359 (1984).
18. Hutchison, C.A., III, Smith, H.O., Pfannkoch, C. & Venter, J.C. Proc. Natl. Acad. Sci. USA 102, 17332–17336 (2005).
DOI:10.1038/nmeth.1318 | NATURE METHODS

© 2009 Nature America, Inc. All rights reserved.

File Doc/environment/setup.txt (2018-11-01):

git config --global user.email "8wan5hrdlu@gmail.com"
git config --global user.name "Peter Reintjes"
sudo apt-get install bluez bluez-tools libbluetooth-dev
sudo apt-get install emacs
git clone git@github.com:eatoin5hrdlu/brewhaha.git
sudo apt-get install imagemagick
cd ~/src/EvoStat/web/images
./emboss <hostname>

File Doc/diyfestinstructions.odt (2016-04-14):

Build your own version of the countme App

Install Java JDK

Install Android Studio

Install Git

Get a copy of the project with the following command line:

git clone https://github.com/eatoin5hrdlu/countme.git

(This creates a directory with the countme Android App and the file appserver.

Start Android Studio

Import Project countme

Generate APK

Generate a QR-code for your phone to find the App: http://zxing.appspot.com/generator/

Select URL and generate a QR code with the text:

http:<your IP address>:8080/countme.apk

Running a Web Server on your Computer:

1) Install swi-prolog

Edit the file appserver to have the right location for the countme.apk file

2) Run swipl and give it the command:

?- [appserver].

Install and run BarcodeReader on your Android phone and point it at the QR-code image.

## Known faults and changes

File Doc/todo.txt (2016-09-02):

Here is my working manifest of pieces and work that need to be done. I'm sorry it is not a concise, pithy description of the few things that need to be done, but I've put an asterisk beside things that are less farther along if you want to call them out specificially.  Everything here has had progress -- (I really tried to find early failures in every sub-system in order to see where the problems will be).

Estimating the time required for individual tasks is always difficult. Sometimes things fall into place and more often things take twice as long.  We've both had enough experience that we can probably take a stab at an appropriately padded schedule.
--------------------
Potential time-saving changes:

Use a machine shop service for specialized metal parts, sparger, heat exchanger, etc.

If the 3D printed parts that I've made work well, we can start ordering them from a service (ShapeWays), so I don't spend any more nights (like last night) cleaning the clogged nozzel on the 3D printer.  Otherwise the schedule would need time allocated to things which would appear to have nothing to do with the EvoStat.
--------------------------

The following will be required for each EvoStat, but at least one prototype for each sub-system has been built and most have two instances but no completely connected system exists yet.

Full integration of the system remains to be done and this will likely require some changes to both hardware and software.  Emphasis has been on keeping the cost low and making the system easy to replicate.  The next phase is to assemble enough of a complete system to start long test runs -- one expected result of these runs may require upgrades to certain components.

For example, even with low-duty-cycle operation, the four $25.00 peristaltic priming pumps may be an early failure point.  These four pumps are required for the three inputs: Host cells, Mutagenisis Inducer (Arabinose), and Selection Inducer (cAMP) -- and one waste/sample output.
(Note: Nutrient pump/valve are not included in the critical flow-rate subsystem because it is independently controlled by the Turbidostat).  Systems with more than three inputs will require a major change, but only if the additional inputs have substantial volumes and thereby need to be part of the flow-rate management.  Small volumes of indicators or innoculant which do not significantly affect the working volume can be handled without additional instrumentation.

The following required for each EvoStat:

Definitions:
   Lagoon - small container for independent evolving viral populations 
   Driver - switched current source to activate a relay or motorDefinitions:
   Supply   - The liquid containers on the top of the EvoStat containing the
              input materials, nutrient and inducers for EvoStat subsystems.
	      This is a collection of containers with bottom output ports
   Cellstat - Subsystem supporting the host cell culture. This includes:
              Heater, mixer, meniscus light, turbidostat, PIR temperature sens,
              Nutrient inlet valve
   Lagoon - The small container for independent evolving viral populations and
            by extension, the subsystem supporting the phage population therein
            including: heater, mixer, meniscus light, four-port input valve for
            host cells and inducers.

   Port   - Lower liquid exit passage for Supply, Cellstat, and Lagoon vessels:
            Ports on all autoclavable vessels must include a disconnect at the end of a
	    length of silicon tubing to avoid stress where the port fitting enters the vessel
            1/8-3/16" diamond-drilled hole in vessel wall
            1/4" silicon tubing gasket inserted into vessel wall
	    One (1) tubing/tubing connection inserted into silicon tubing gasket
	    Minimum 2-4" silicon tubing to mechanically separate the disconnect from vessel
	    One (1) tubing to Luer-lock disconnect fitting.

   Sampler - The sample collector and outflow valve controller for both lagoon
             and cellstat outflow rates.

   Driver - Any of several switched current sources to activate a relay or motor

   Solid-state relay - 3-5volt DC controlled line-voltage, high-current relays for
	       Heater power supply (36 VAC transformer)
	       Aeration system (Aquarium Air pump)

Containers/Septa:
   1 Cellstat Vessel, 1-2L transparent glass with:
      a) Three (3) top inflow Ports 
      b) Five (5) lower outflow Ports
   1-4 Lagoon Vessels, 250mL transparent glass with single lower exit Port
   1-4 3D printed septa Lagoons w/2-4 inlets.

Heating:  
    Heater for host cell container
    Melexis (PIR) temperature detector
    1 high-voltage solid state relay
    1-4 (low-voltage) heaters for lagoons
    (Still possible we will want a chamber heater. E.g. Heat Gun w/ relay)
    Drivers for Arduino control of all heating elements
    Software

Mixing:
    Magnetic mixer for Host cell container
    4 magnetic mixers for lagoons
    Drivers for five mixing motors
    Software

Containers:
   1 3D printed cap with septa for host cell container
   4 3D printed caps for 250mL lagoons
   4 3D printed caps for 100mL lagoons

Heating:  
    Heater for host cell container
    Melexis (PIR) temperature detector
    1 high-voltage solid state relay
    4 (low-voltage) heaters for lagoons
    1 in-line heater for nutrient
    1 in-line heater for inducer
    Drivers for Arduino control of all heating elements
    Software

Mixing:
    Magnetic mixer for Host cell container
    4 magnetic mixers for lagoons
    Drivers for five mixing motors
    Software

Aeration:
    Two (2) stainless steel sparger arcs for host cell container
    One (1) Aquarium air-pump
    One (1) High-voltage solid-state relay for air-pump

Flow
    Drivers for:
     	    Nutrient valve
	    Inducer valve
	    Host cell valve
	    Four (4) Five (5) position pinch valves for Lagoons
	    Outflow valve

Optics:
    Drivers for red, yellow, green, blue, and red laser LEDs
    Arduino Software for light control
    Light-tight insulation for thermal enclosure
    System Software (OpenCV) for:
        Level detection
        Turbidity Measurement
	Fluorescence

Software:
    Distributed Temperature control
    Turbidity/Nutrient supply control
    Level/Flow maintenance
    Leak detection
    Data logging
    Text messaging

Stainless steel upgrade:

The EvoStat super-structure uses PVC for all vertical structure and black-iron pipe for strong horizontal platforms (e.g. Supply platform).  Black-iron fittings should be replaced with stainless steel (at approx 4X cost).

I have initial versions of software for the pump control software on micro-controllers and level detection on system computer, but integration of optical sensing and flow control is still to be done.

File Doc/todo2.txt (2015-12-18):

Here is my working manifest of pieces and work that need to be donto do. I'm sorry it is not a concise, pithy description of the few things that need to be done, but I've put an asterisk beside things that are less farther along if you want to call them out specificially.  Everything here has had progress -- (I really tried to find early failures in every sub-system in order to see where the problems will be).

Estimating the time required for individual tasks is always difficult. Sometimes things fall into place and more often things take twice as long.  We've both had enough experience that we can probably take a stab at an appropriately padded schedule.
--------------------
Potential time-saving changes:

Use a machine shop service for specialized metal parts, sparger, heat exchanger, etc.

If the 3D printed parts that I've made work well, we can start ordering them from a service (ShapeWays), so I don't spend any more nights (like last night) cleaning the clogged nozzel on the 3D printer.  Otherwise the schedule would need time allocated to things which would appear to have nothing to do with the EvoStat.
--------------------------

The following will be required for each EvoStat, but at least one prototype for each sub-system has been built and most have two instances but no completely connected system exists yet.

Full integration of the system remains to be done and this will likely require some changes to both hardware and software.  Emphasis has been on keeping the cost low and making the system easy to replicate.  The next phase is to assemble enough of a complete system to start long test runs -- one expected result of these runs may require upgrades to certain components.

For example, even with low-duty-cycle operation, the four $25.00 peristaltic priming pumps may be an early failure point.  These four pumps are required for the three inputs: Host cells, Mutagenisis Inducer (Arabinose), and Selection Inducer (cAMP) -- and one waste/sample output.
(Note: Nutrient pump/valve are not included in the critical flow-rate subsystem because it is independently controlled by the Turbidostat).  Systems with more than three inputs will require a major change, but only if the additional inputs have substantial volumes and thereby need to be part of the flow-rate management.  Small volumes of indicators or innoculant which do not significantly affect the working volume can be handled without additional instrumentation.

Definitions:
   Lagoon - small container for independent evolving viral populations 
   Driver - switched current source to activate a relay or motor

Containers/Septa:
   1 3D printed cap with septa for host cell container
   * 4 3D printed caps for 250mL lagoons
   * 4 3D printed caps for 100mL lagoons

Heating:  
    Heater for host cell container
    Melexis (PIR) temperature detector
    1 high-voltage solid state relay
    * 4 (low-voltage) heaters for lagoons
    * 1 in-line heater for nutrient
    1 in-line heater for inducer
    * Still possible we will want a chamber heater. E.g. Heat Gun w/ relay
    Drivers for Arduino control of all heating elements
    Software

Mixing:
    Magnetic mixer for Host cell container
    4 magnetic mixers for lagoons
    Drivers for five mixing motors
    Software

Aeration:
    2 stainless steel sparger arcs for host cell container
    1 Aquarium air-pump
    1 High-voltage solid-state relay for air-pump

Flow
    12 3D printed compression valves
    1  3D-printed pointer
    1  3D-printed motor bracket
    Drivers for:
    	    Nutrient valve and pump
	    Inducer valve and pump
	    Host cell valve and pump
	    Outflow valve and pump
    Driver for Rotary valve unit (torque control)
    Step-encoder resistor network
    Software for position sensing and torque control

Optics:
    Drivers for red, yellow, green, blue, and red laser LEDs
   * Arduino Software for light control
   * Light-tight insulation for thermal enclosure
    System Software (OpenCV) for:
        Level detection
       * Turbidity Measurement
       * Fluorescence

Software:
    * Distributed Temperature control
    Turbidity/Nutrient supply control
    * Level/Flow maintenance (3 inputs)
    *  Leak detection  (sensors below apparatus)
    *  Data logging 
    Text messaging

There can be a structural stainless-steel version, currently all structure is PVC.

I have initial versions of software for the pump control software on micro-controllers and level detection on system computer, but integration of optical sensing and flow control is still to be done.

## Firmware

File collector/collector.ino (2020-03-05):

// Sample Collector and Drain Valves

#define P(x)  Serial.print(x)
#define PL(x) Serial.println(x)

int overflow_sensor[2] = { A0, A7 };
int overflow_valve[2]  = { A1, A2 };

char id = 'a'; // s is default for supply

#define EOT "end_of_data."

void printInterface()
{
  PL(F("i( sampler, ebutton,\n\
      [ rw(up, int:=90,   \"Update every 90 seconds\"),\n\
	rw(al, int:=10,   \"Aliquot time in seconds\"),\n\
	rw(ns, int:=24,   \"Number of samples\"),\n\
	rw(ts, int:=3600, \"Time to next sample\"),\n\
	rw(pd, int:=90,   \"Drain Timing Interval\"),\n\
	rw(gt, int:=3600, \"Group Time\"),\n\
	rw(gn, int:=1,    \"Group Number\"),\n\
        rw(v0, int:=1000, \"Host Drain Valve Timing\"),\n\
        rw(v1, int:=1000, \"Lagoon1 Drain Valve Timing\"),\n\
        rw(v2, int:=1000, \"Lagoon2 Drain Valve Timing\"),\n\
        rw(v3, int:=1000, \"Lagoon3 Drain Valve Timing\"),\n\
        rw(v4, int:=1000, \"Lagoon4 Drain Valve Timing\")\n\
       ])."));
}

      
// Requires Arduino with:
// Two interrupt pins: Home photo-interruptor(pin 2) and Encoder A input (pin 3)
// Two inputs for Encoder B (pin 4) and sample platform endstop (pin 6).
// Four outputs for the phases of the sample platform stepper (8-11)
// Five outputs for the drains of Lagoons 1-4 and the CellStat (A1-A5).
// 
// 1) Set Start Time
// 2) Set number of samples and times
//
//
// Pin numbers currently for Ardweeny
//
// Maxon Motor Encoder 8-pin header pinout
// (Red stripe) Pin 1: Motor (+)
//              Pin 2: Shield
//              Pin 3: Channel B
//              Pin 4: Vcc Enc (5V)
//              Pin 5: Channel A
//              Pin 6: Gnd Enc
//              Pin 7: Shield
//              Pin 8: Motor (-)
//
#define digitalPinToInterrupt(p)  (p==2?0:(p==3?1:(p>=18&&p<=21?23-p:-1)))
#define NUM_VALVES 5
#define HOSTFULL   A0   /* Analog liquid level sensor */
#define LAGOONFULL A2   /* Analog liquid level sensor */
//
// The following numbers work for the 12-volt motor supply
// With four tubes to compress, 5-volts wasn't enough torque
// These numbers should be stored in EEPROM and re-programmable
//

#define FULL_POWER   240
#define MEDIUM_POWER 180
#define LOW_POWER    120
#define PWM_OFF        0

#define ENCODER_180  400  // PWM Power and this are GearMotor dependent

#define ARDWEENY 1
#ifdef ARDWEENY
const int drivePin = 5; // DC motor, PWM with three power levels
const int closePin = 2; // PIN with ISR for photo-interrupter
const int countPin = 3; // PIN with ISR for Gearmotor Encoder Phase A
const int phaseB   = 4; // PIN                        Encoder Phase B

const int ENDSTOP    =  6;
const int SAMPLE_SPACE = 54;
const int GROUP_SPACE = 100;

// Stepper Phases: forward (1-3-2-4) reverse (4-2-3-1)
const int P1 =  8;
const int P2 =  9;
const int P3 = 10;
const int P4 = 11;

#endif

const int DEFAULT_VALVECYCLE = 60000UL;
const int DEFAULT_SAMPLES    = 24;
const int DEFAULT_SAMPLETIME = 3600UL;
const int DEFAULT_ALIQUOT    = 500UL;

#define EOT     "end_of_data."
#include <EEPROM.h>
const boolean debug     = false;
      boolean firstTime = true;

// Set global 'RomAddress' and address will be bumped
// by successive calls to moveData( SAVE|RESTORE, size, ptr)
const int      SAVE   = 1;
const int   RESTORE   = 0;
      int   RomAddress;
//
//
volatile int state;

const int STARTUP  = 0;
const int CLOSED   = 1;
const int COUNTING = 2;
const int OPENED   = 3;
const int CLOSING  = 4;

char *statename[] = {
	"STARTUP",
	"CLOSED",
	"COUNTING",
	"OPENED",
	"CLOSING",
};
// Interrupt variables and service routine (ISR)
volatile boolean closedPosition;                               // BOOLEAN 
void             closed_position() { closedPosition = true; }  // photointerrupter

volatile int     ENCODER_count;
int              last_ENCODER_count;

void encoderA()                   // Interrupt on Phase A  0 -> 1
{
//	if (digitalRead(phaseB))  // If (Phase B is HIGH)
	   ENCODER_count++;           //        rotation is CCW
}

unsigned long openInterval = 1000UL;          // 3 seconds
 
unsigned long now;
unsigned long lastTime;
unsigned long lastSampleTime;
unsigned long onTime;
unsigned long cycleTime;
unsigned long valveCycle;
unsigned long lastValveCycle;


// Platform Control

int sampleTime;    // Time between samples
int sampleNum;     // Total number of samples to take
int groupNum;      // Number of samples per group
int groupTime;     // Time between groups
int aliquot;       // Milliseconds for sample taking
unsigned int valveInterval;
int valveTime[6]; // Valve open time in milliseconds per interval
int valvePin[6]; // Valve open time in milliseconds per interval
int updateTime;

int sampleCountdown; // Set to SampleNum after RESET
unsigned long int sampleTimeMS;


void printHelp(void)
{
	Serial.println("a(value,'aliquot - extraction in msec').");
	Serial.println("c('clear - reset platform/start sampling').");
	Serial.println("d('dump (print) settings').");
	Serial.println("e(value,'time between sample groups').");
	Serial.println("g(value,'number of samples in group').");
	Serial.println("h('help - print this command menu').");
	Serial.print("i(");Serial.print(valveTime[0]);Serial.println(",'set lagoon1 drain time(ms)').");
	Serial.print("j(");Serial.print(valveTime[1]);Serial.println(",'set lagoon2 drain time(ms)').");
	Serial.print("k(");Serial.print(valveTime[2]);Serial.println(",'set lagoon3 drain time(ms)').");
	Serial.print("l(");Serial.print(valveTime[3]);Serial.println(",'set lagoon4 drain time(ms)').");
	Serial.print("m(");Serial.print(valveTime[4]);Serial.println(",'set cellStat drain time(ms)').");
	Serial.print("n(");Serial.print(sampleNum);Serial.println(",'total number of samples').");
	Serial.print("p("); Serial.print(valveInterval);Serial.println(",'set drain timing interval').");
	Serial.print("t("); Serial.print(sampleTime); Serial.println(",'time between samples').");
	Serial.println("s('save current settings').");
	Serial.println("r('restore stored settings').");
	Serial.println("z('zero EEPROM - defaults restored after reset').");
}

// BEGIN DEFAULT CALIBRATION PARAMETERS
// Values will be read from EEPROM, after being saved with the 's' command.
// Values below are the defaults before they are saved to EEPROM or 
// after using the 'z' command to zero the EEPROM.


const int MT = 7;  // mS delay between stepper motor phase shifts

void reset()
{
int toolong = 100;
	if (debug) Serial.print("reset(start).");
	while(digitalRead(ENDSTOP) && toolong--)
	{
		reverse(10);
		respondToRequest();
	}
	sampleCountdown = sampleNum;  // Reset to start sample count
	if (debug) {
		if (toolong < 1) Serial.println("reset(timeout).");
		Serial.println("reset(finished).");
	}
}

void setvpin(int v,int p)
{
  pinMode(p,OUTPUT);
  digitalWrite(p,0);
  valvePin[v] = p; 
}

int ctr;
void setup()
{
int i;
	Serial.begin(9600);
	
	// Sampler Pins
//	pinMode(drivePin, OUTPUT);
	analogWrite(drivePin, PWM_OFF);

	pinMode(closePin, INPUT);
	pinMode(countPin,  INPUT);
	pinMode(phaseB,    INPUT);

        // Five Drain Valves
	setvpin(0,A1);
	setvpin(1,A2);
	setvpin(2,A3);
	setvpin(3,A4);
	setvpin(4,A5);
	setvpin(5,A6);
	
	closedPosition = false;
	lastTime = millis();
	ctr = 0; 
	state = STARTUP;

	// Platform Control

	pinMode(P1, OUTPUT);	digitalWrite(P1,    0);
	pinMode(P2, OUTPUT);	digitalWrite(P2,    0);
	pinMode(P3, OUTPUT);	digitalWrite(P3,    0);
	pinMode(P4, OUTPUT);	digitalWrite(P4,    0);
	pinMode(ENDSTOP,        INPUT_PULLUP);

	RomAddress  = 0;
	if (EEPROM.read(0) == 0 or EEPROM.read(0) == 255) // firsttime
	{
		if (debug)
		   Serial.print("Setting defaults in EEPROM.");

		sampleTime = DEFAULT_SAMPLETIME;// Seconds between samples
		sampleNum  = DEFAULT_SAMPLES;   // Two 96-well plates lengthwise
		groupNum   = 12;                // Number of samples per group
		groupTime  = 0;                 // Time between groups
		aliquot = DEFAULT_ALIQUOT;      // SAMPLE SIZE in mSec
		for (i=0; i< 6; i++) valveTime[i] = 800;
		valveInterval = DEFAULT_VALVECYCLE;
		saveRestore(SAVE);
	}
	saveRestore(RESTORE);
	sampleTimeMS = sampleTime*1000UL;  // Sampling interval in milliseconds
	openInterval = aliquot;
	if (debug)
		printHelp();
	lastSampleTime = millis(); // Wait long interval for first sample
	reset();
}

void forward(int steps)
{
	for(int i=0; i<steps; i++) {
		digitalWrite(P1, 1);
		delay(MT);
		digitalWrite(P4, 0);
		delay(MT);
		digitalWrite(P3, 1);
		delay(MT);
		digitalWrite(P1, 0);
		delay(MT);
		digitalWrite(P2, 1);
		delay(MT);
		digitalWrite(P3, 0);
		delay(MT);
		digitalWrite(P4, 1);
		delay(MT);
		digitalWrite(P2, 0);
		delay(MT);
	}
	digitalWrite(P4, 0);
}

void reverse(int steps)
{
	for(int i=0; i<steps; i++) {
		digitalWrite(P4, 1);
		delay(MT);
		digitalWrite(P1, 0);
		delay(MT);
		digitalWrite(P2, 1);
		delay(MT);
		digitalWrite(P4, 0);
		delay(MT);
		digitalWrite(P3, 1);
		delay(MT);
		digitalWrite(P2, 0);
		delay(MT);
		digitalWrite(P1, 1);
		delay(MT);
		digitalWrite(P3, 0);
		delay(MT);
	}
	digitalWrite(P1, 0);
}


void flash(void)
{
        digitalWrite(13,1);
	delay(300);
	digitalWrite(13,0);
}

void moveData(int op, int size, byte *loc)
{
	for(int i=size;i>0;i--)
		if (op == SAVE)
			EEPROM.write(RomAddress++,*loc++);
		else
			*loc++ = EEPROM.read(RomAddress++);
}

void saveRestore(int op)
{
	int i;
	RomAddress = 0;
	if (op == RESTORE and (EEPROM.read(0) == 0 or EEPROM.read(0) == 255))
	{
	  if (debug)
	    Serial.println("Cannot RESTORE from uninitialized zero EEPROM");
	  return;
	}
	moveData(op, sizeof(int), (byte *)&sampleTime );
	moveData(op, sizeof(int), (byte *)&sampleNum );
	moveData(op, sizeof(int), (byte *)&groupNum );
	moveData(op, sizeof(int), (byte *)&groupTime );
	moveData(op, sizeof(int), (byte *)&aliquot );
	moveData(op, sizeof(int), (byte *)&valveInterval );
	moveData(op, 6*sizeof(int), (byte *)&valveTime );
}

void dump(void)    // Print configuration settings
{
  int i;
  Serial.print("t "); Serial.println(sampleTime);
  Serial.print("n "); Serial.println(sampleNum);
  Serial.print("g "); Serial.println(groupNum);
  Serial.print("a(ms) "); Serial.println(aliquot);
}

void respondToRequest(void)
{
	String is = "";
	while (Serial.available() > 0)  // Read a line of input
	{
		int c  = Serial.read();
		if ( c < 32 ) break;
		is += (char)c;
		if (Serial.available() == 0) // It is possible we're too fast
			delay(100);
	}
	if ( is.length() > 0 )  {   // process the command
		int value = 0;
		if (is.length() > 2) {
			value = atoi(&is[2]);
			if (value == 0) value = 1;
		}
		process(is[0], is[1], value);
	}
}

void printTermInt(char *functor, int arg)
{ Serial.print(functor); Serial.print("(");Serial.print(arg);Serial.println(")."); }

void printTermUInt(char *functor, unsigned int arg)
{ Serial.print(functor); Serial.print("(");Serial.print(arg);Serial.println(")."); }

void printTerm2Int(char *functor, int arg1, int arg2)
{ 
  Serial.print(functor); Serial.print("(");
  Serial.print(arg1);Serial.print(",");
  Serial.print(arg2);Serial.println(")."); 
}
void printTermChar(char *functor, char arg)
{ Serial.print(functor); Serial.print("(");Serial.print(arg);Serial.println(")."); }

unsigned long int
elapsed(unsigned long int cur_time, unsigned long int prev_time)
{
   if (cur_time < prev_time)   // handle rollover
      return( cur_time - *( (long int *)&prev_time ) );
   else
      return ( cur_time - prev_time );
}
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

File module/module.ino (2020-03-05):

#include "param.h"
#if (ARDUINO >= 100)
 #include "Arduino.h"
#else
 #include "WProgram.h"
#endif
// All Innatrix Arduino control programs contain at least:
//
//   void respondToRequest(void)
//   bool process_command(char c1, char c2, int value)
//   void setup()
//   void loop()
//
//  If DOWNLOADING this program fails:
//
//  1) Disconnect Bluetooth (it competes with USB cable for RX/TX)
//  2) Disconnect RESET wire (without Bluetooth module, Reset held low)
//  3) Check Tools->Processor for Bootloader compatibility

#include <Wire.h>
#include <Adafruit_Sensor.h>   // Arduino: Manage Libraries
#include <Adafruit_TSL2591.h>

Adafruit_TSL2591 tsl;
int gain_setting;   // Luminometer Gain
int timing_setting; // Integration Time
boolean luxOn;

tsl2591Gain_t
tsl_gain[4] = { TSL2591_GAIN_LOW,   //    1X
	        TSL2591_GAIN_MED,   //   25X
		TSL2591_GAIN_HIGH,  //  428X
		TSL2591_GAIN_MAX }; // 9876X

tsl2591IntegrationTime_t
tsl_timing[6] = { TSL2591_INTEGRATIONTIME_100MS,
	          TSL2591_INTEGRATIONTIME_200MS,
		  TSL2591_INTEGRATIONTIME_300MS,
		  TSL2591_INTEGRATIONTIME_400MS,
		  TSL2591_INTEGRATIONTIME_500MS,
		  TSL2591_INTEGRATIONTIME_600MS };

void lux_set_timing(int t)
{
  if (t < 0 || t > 5)
     printTermInt("e",101);
  else if (luxOn)
  {
	tsl.setTiming(tsl_timing[t]);
	timing_setting = t;
  }
  else 
       printTermInt("e",99);
}

void lux_set_gain(int g)
{
   if (g < 0 || g > 3 )
      printTermInt("e",100);
   else if (luxOn) {
   	tsl.setGain(tsl_gain[g]);
	gain_setting = g;
   } else
     printTermInt("e",98);
}

void lux_init(int id)
{
  tsl  = Adafruit_TSL2591(id); // pass in id (for you later)
  if (tsl.begin())
  {
        luxOn = true;
	tsl.setGain(tsl_gain[gain_setting]);
	tsl.setTiming(tsl_timing[timing_setting]);
  }
}

int luxGain(void) // 0-3
{
  int i;
  tsl2591Gain_t gainval = tsl.getGain();
  for(i=0;i<4;i++)
    if (gainval == tsl_gain[i]) return i;
  return -1;
}

int luxTiming(void) // mSeconds
{
  return((tsl.getTiming() + 1)*100);
}

void lux_details()
{
    sensor_t sensor;
    tsl.getSensor(&sensor);
    Serial.print  ("Sensor:    "); Serial.println(sensor.name);
    Serial.print  ("Driver Ver:"); Serial.println(sensor.version);
    Serial.print  ("Unique ID: "); Serial.println(sensor.sensor_id);
    Serial.print  ("Max Value: "); Serial.print(sensor.max_value);
    Serial.println(" lux");
    Serial.print  ("Min Value: "); Serial.print(sensor.min_value);
    Serial.println(" lux");
    Serial.print  ("Resolution:"); Serial.print(sensor.resolution);
    Serial.println(" lux");  
    Serial.println("------------------------------------");
}

uint16_t luxRaw(void)
{
	if (luxOn)
	   return(tsl.getLuminosity(TSL2591_FULLSPECTRUM));
	else
	   return(0);
  //    return(tsl.getLuminosity(TSL2591_VISIBLE));
  //    return(tsl.getLuminosity(TSL2591_INFRARED));
}

boolean auto_temp;   // Automatically control Heater
boolean auto_valve;  // Automatically control Valves
boolean auto_mixer;  // Automatically control Mixer
boolean auto_air;    // Automatically control Aeration
boolean mixer_state;
 
char reply[40];

/* EEPROM SAVE AND RESTORE OF ID AND CALIBRATION CONSTANTS */

#include "EEPROM.h"
int eeSize;
int RomAddress  = 0;

byte id = 'm'; // module: generic, by default
int target_temperature;
int target_turbidity;
int target_flowrate;
int gtscale;
int gtoffset;  // Offset and scale for Turbidity calculation
int OD;
int interval;   // Variable to keep track of the time

int led600int = 200;
int laserint  = 200;
int meniscusint = 200;

int mixerspeed;
int reading[10];
boolean dflag = false;
int drate;
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

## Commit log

2015-12-18 Initial checkin of EvoStat (renamed from PACE)
    [ADriver.sch, PControl.sch, Pulley10mm10t.scad, Pulley6mm9t.scad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]
2015-12-30 new combined collector platform and sampler code
2016-01-04 Modular AutoSampler frame
    [auto.scad]
2016-01-09 drain valve timing added
2016-01-11 24 sample end condition
2016-01-14 BIG documentation
    [Budget.ods, Budget.xlsx]
2016-01-19 lagoon servo and removed drain valve
2016-01-22 12-volt settings
2016-01-28 curtain rod added
    [auto.scad, core4.scad]
2016-01-31 budget and prop edits
    [Budget.ods]
2016-02-01 blackout shroud for luminosity tubes
    [lumtubes.scad]
2016-02-03 changes to proposal and budget
    [Budget.ods]
2016-02-08 photo-board, curtain rod, larger bearing hole
    [auto.scad]
2016-02-08 larger mounting screw
    [auto.scad]
2016-02-08 merged SS version
    [auto.scad]
2016-02-09 curtain, bearing, photo-interruptor board
    [auto.scad]
2016-02-09 space for set-screw
    [auto.scad]
2016-02-11 new pictures/cad files
    [cryocam.scad]
2016-02-11 new grant draft
    [Budget.xlsx]
2016-03-05 show socket
2016-03-05 new angled dremelfuge
    [dremelfuge.scad]
2016-03-06 angled tubes
    [fatdremelfuge.scad]
2016-03-06 larger fat
    [fatdremelfuge.scad]
2016-03-07 socket communication cleanup
2016-03-07 larger hole
    [fatdremelfuge.scad]
2016-03-16 reconnect on bluetooth socket failure
2016-03-17 new lagoon wiring
2016-03-19 flow adjustments
2016-03-21 direct setting of valve time
2016-03-21 printHelp() added, #ifdef'd out WiFi (reduce space)
2016-03-22 query valves fixed
2016-03-25 powerup servo on manual position override
2016-03-29 added real MLX temperature to simulated platform
2016-03-30 sampler error handling, timing issues
2016-03-31 temperature and servo commands
2016-04-03 moved baffle
    [mirrorpla.scad]
2016-04-07 camera param
2016-04-10 New two-part mirror holder
    [mirrorclam.scad]
2016-04-21 valve time adjustment
2016-04-29 new valve report for lagoons
2016-04-30 mixerspeed valve io
2016-05-01 failed to clear temperature/3 for lagoon
2016-05-17 update path from web to Arduinos
2016-05-18 edit parameters for all devices
2016-05-29 new angled turbidostat sensor
    [cellstatalpha.scad]
2016-05-30 beta turbo and baffle design
    [baffle11.scad, cellstatbeta.scad]
2016-05-30 rounded, stable
    [baffle11.scad]
2016-05-31 shallow magnet holes
    [cellstatgamma.scad]
2016-06-02 testing turbidity, print statements
2016-06-03 remove unconnected devices from change page
2016-06-05 larger nutholes, deeper magholes
    [cellstatdelta.scad]
2016-06-07 trimmed down
    [cellstatepsilon.scad]
2016-07-07 7.8mm radius jar
    [cellstatzeta.scad]
2016-07-31 review printout
2016-08-19 longer valve interval(60s),shorter default valve times(800ms)
2016-09-05 setscrew added
    [cellstateta.scad]
2016-09-10 pitch and yaw setscrews
    [cellstatheta.scad]
2016-09-12 pitch and yaw added
    [cellstatiota.scad]
2016-09-15 steeper angle for turbid
    [cellstatkappa.scad]
2016-09-15 host didn't have temperature setting?
2016-10-05 camera CGI SDK
2016-10-05 center camera
2016-10-22 arduino driven iface
2016-11-22 new check in
    [turbintemp.scad]
2016-11-23 new ch
    [cuvetteholder.scad]
2016-11-26 new coli
    [ecoliseum.scad]
2016-12-01 macro lens holder for Hero 5/Lux Pro 450
    [macro.scad]
2016-12-05 trimmed Hero 5 Macro lens
    [macro2.scad]
2016-12-09 new flowcell cap
    [flowcap.scad]
2016-12-09 rotated flowcell cap
    [flowcap.scad]
2016-12-10 fourth try
    [flowcap4.scad]
2016-12-10 no luer
    [nipplecap.scad]
2017-01-14 lagoon temp and valve terms fixed
2017-01-15 sampler protocol
2017-01-16 new clips
    [clip.scad, clip0.scad]
2017-01-19 return servo angle settings d-command
2017-01-22 parsing arduino out
2017-01-27 cuvettes added
    [cuvettebulge.scad, cuvettebulge2.scad]
2017-01-28 timing valves
2017-01-28 valve timing issues, updates stop when using dialin arduino dialog
2017-01-29 streamlined re-connect sockets
2017-02-03 sampler returning id/iface
2017-02-05 flow and level detection tweaks
2017-02-10 adding luminosity prototype code
2017-02-12 flow rate min/max web edit
2017-02-16 flow tweaks, %levels, contrast
2017-02-16 flow PID
2017-02-16 Separate flow logging
2017-02-17 new level/flow tweaks
2017-02-18 many flow bugs caught and killed
2017-02-18 put flow log into web directory
2017-02-25 fluorescence and digital temperature lagoon
2017-03-27 lum holder
    [luminometer.scad]
2017-04-06 wiring update
2017-04-06 printable version
2017-04-08 second wiring harness for cellstat described
2017-04-18 reversed servo pins/debugging output for bluetooth
2017-05-08 upside clip
    [newclip.scad]
2017-08-30 flow features, camera reset
2017-08-30 flow logging
2017-08-30 filter out leak 500 glitch
2017-09-05 refactored pin assignment
2017-09-15 model and flow fixes
2017-09-26 new intialization of valve timings
2017-10-26 Laser pattern for Delrin pinch-valve components
2017-12-22 air supply
    [customizable_hose_tee.scad]
2017-12-27 new doc
    [customizable_hose_tee.scad]
2017-12-29 array for patent
    [ecoliseumarray.scad]
2018-02-27 added vertical line measurement for 2mL precision
2018-11-07 Modulo valves added
2018-11-26 file leak, new camera settings, lagoon interface to turbidity added
2018-11-28 Close bluetooth sockets before restart
2018-12-19 new temperature handling
2019-01-08 long int valve timing fixed
2019-01-21 Arduino var web interface, no GUI image update without user interaction (100seconds)
2019-01-26 more error recovery in parsing terms from Arduino
2019-01-28 Takes CSV file and creates plot of temperatures over EvoStat Run
2019-02-13 arduino print interface
2019-03-02 Sensor.h removed
2019-07-05 wiring document
2019-09-30 Plumbing diagram for peristaltic pump-based EvoStat
2019-10-02 Pump version documentation
2020-03-05 sensitive data purge
    [Budget.ods, Budget.xlsx, auto2.scad, customizable_hose_tee.scad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]
